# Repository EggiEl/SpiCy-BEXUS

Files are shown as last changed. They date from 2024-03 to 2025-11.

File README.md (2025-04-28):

# SpiCy-BEXUS
Please take a look at the [wiki](https://github.com/EggiEl/SpiCy-BEXUS/wiki) for documentation of electrical and software.

### About
This is the official GitHub repository of the SpiCy-BEXUS team, dedicated to code sharing and documentation for our project.

<table align="center">
  <tr>
    <td align="center">
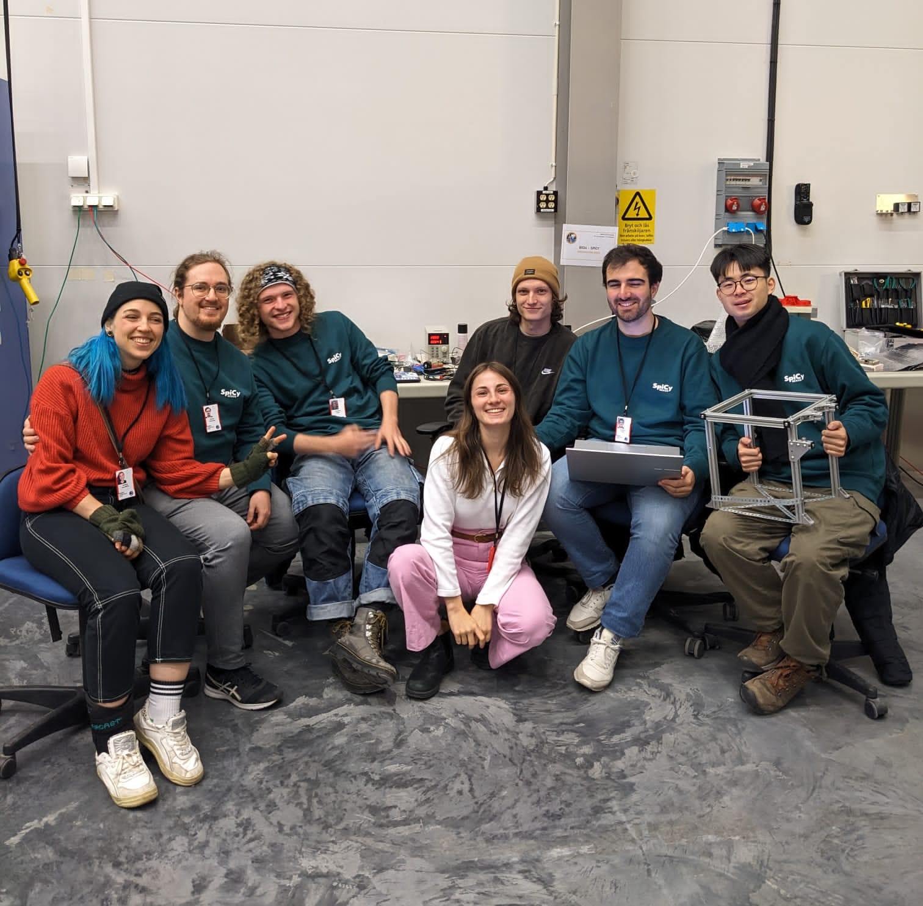
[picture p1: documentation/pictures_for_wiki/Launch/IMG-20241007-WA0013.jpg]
      
    </td>
    <td align="center">
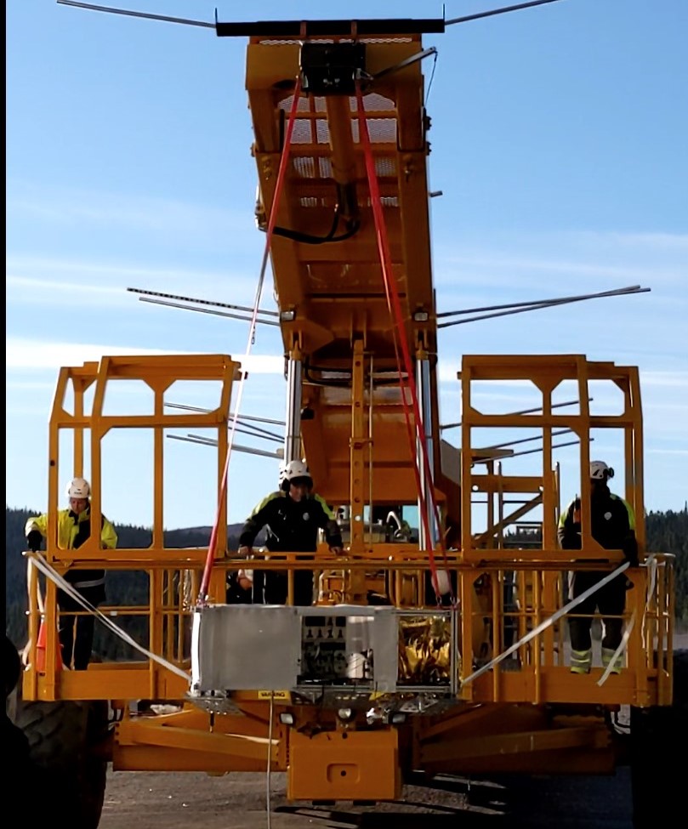
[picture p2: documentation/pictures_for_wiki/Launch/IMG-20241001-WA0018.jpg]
      
    </td>
    <td align="center">
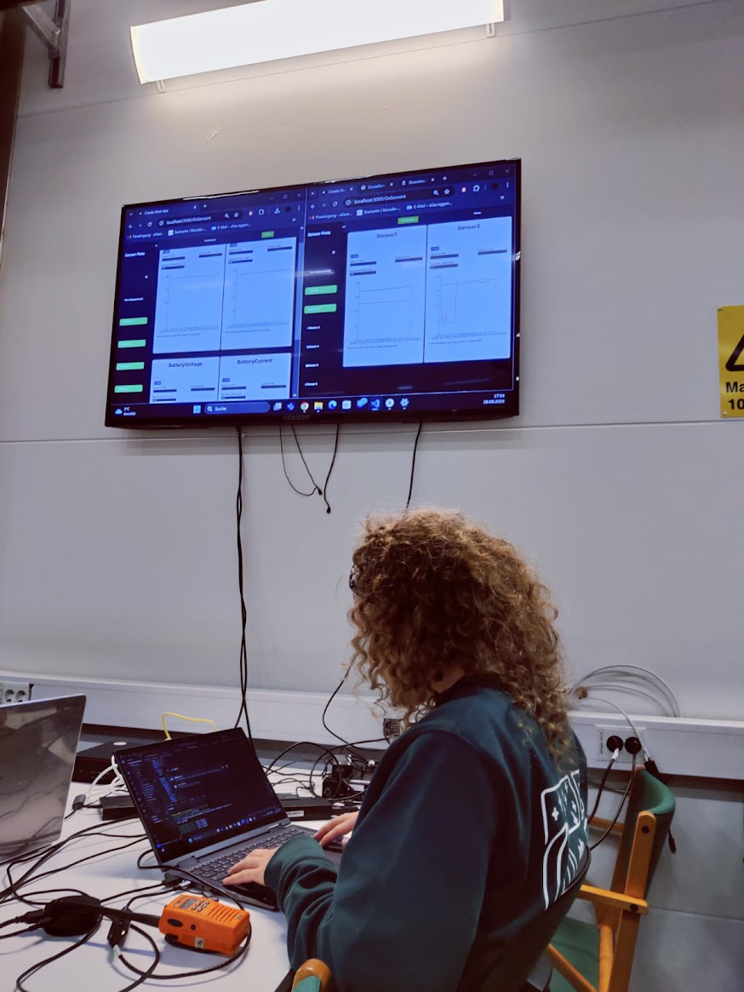
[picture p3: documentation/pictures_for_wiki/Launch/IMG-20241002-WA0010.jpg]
      
    </td>
  </tr>
  <tr>
    <td align="center">
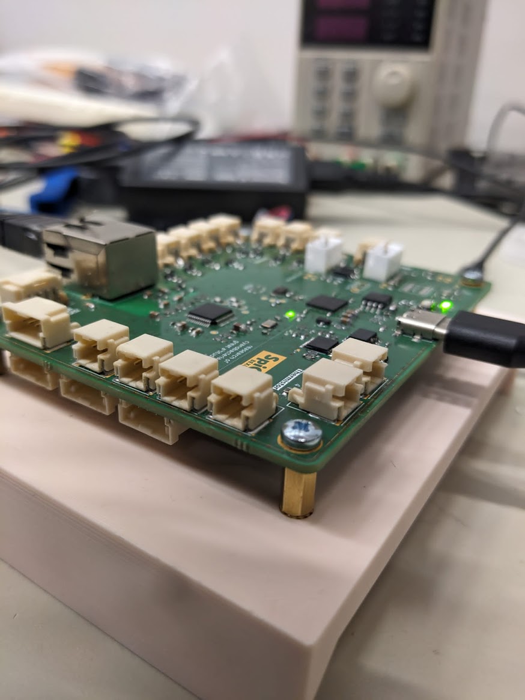
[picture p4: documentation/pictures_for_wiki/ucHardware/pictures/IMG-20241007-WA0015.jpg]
      
    </td>
    <td align="center">
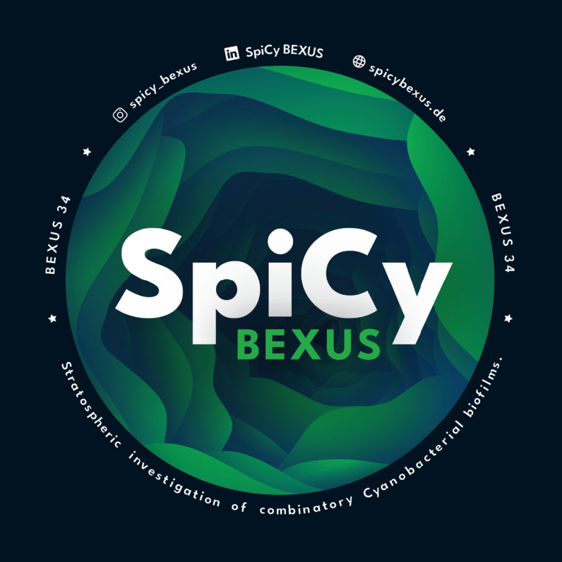
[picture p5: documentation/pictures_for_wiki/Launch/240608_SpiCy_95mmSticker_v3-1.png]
      
    </td>
    <td align="center">
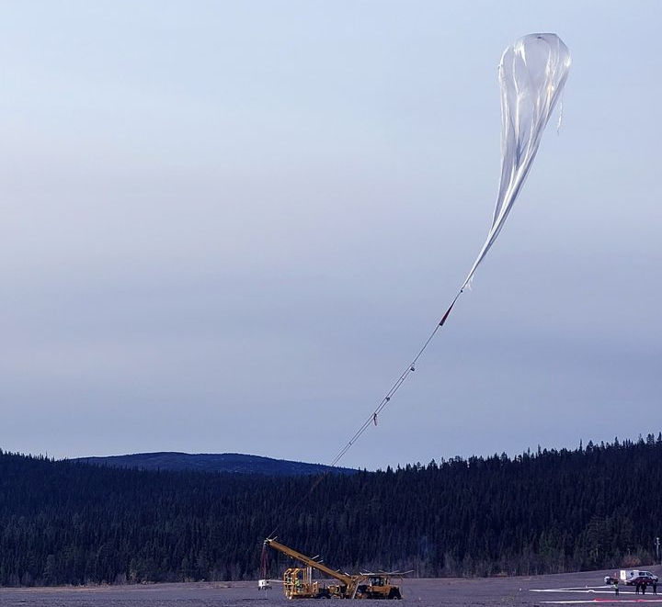
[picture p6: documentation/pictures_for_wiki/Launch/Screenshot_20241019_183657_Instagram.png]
      
    </td>
  </tr>
  <tr>
    <td align="center">
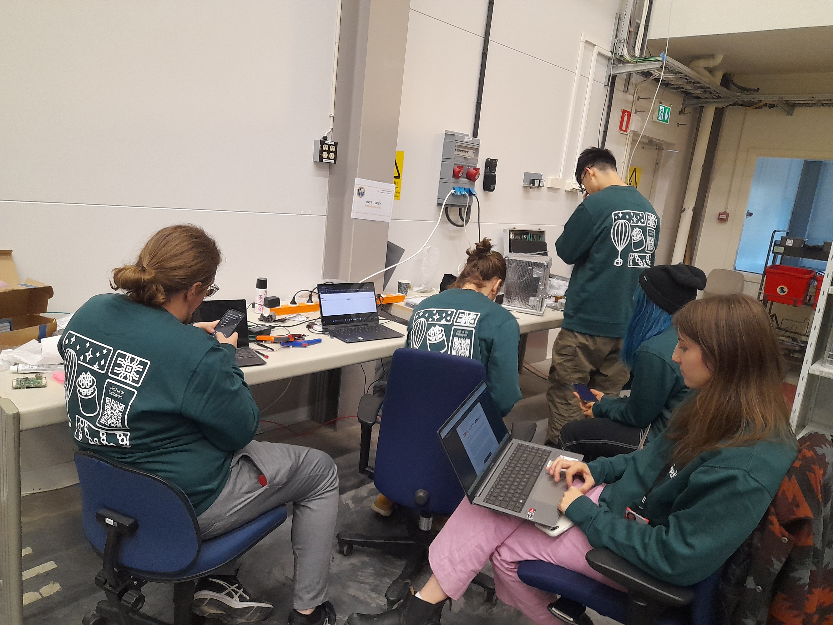
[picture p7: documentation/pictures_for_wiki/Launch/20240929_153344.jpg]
      
    </td>
    <td align="center">
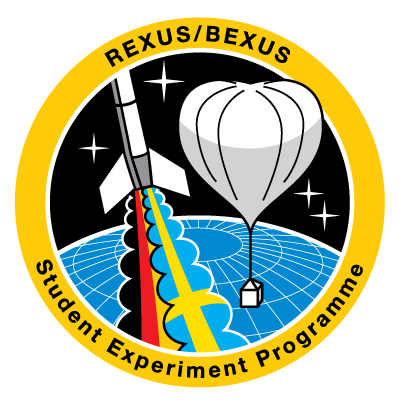
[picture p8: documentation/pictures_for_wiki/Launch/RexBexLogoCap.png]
RexBex Logo
      
    </td>
    <td align="center">
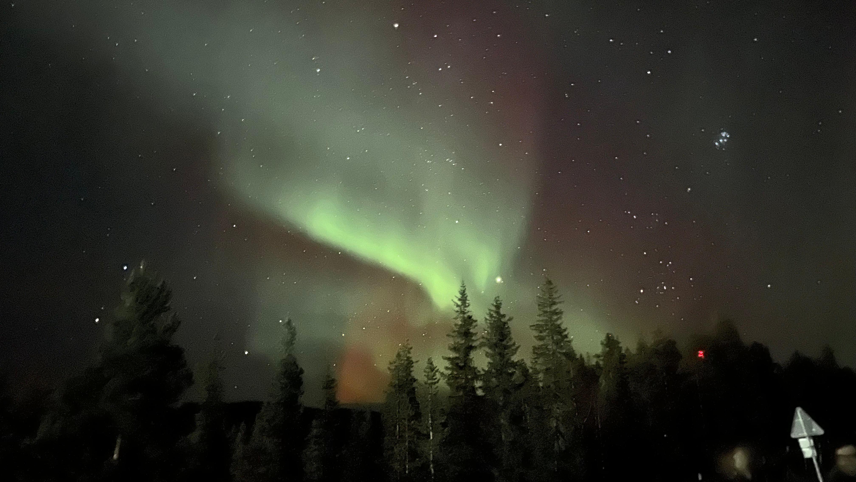
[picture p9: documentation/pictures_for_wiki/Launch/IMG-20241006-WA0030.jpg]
      
    </td>
  </tr>
</table>

### Project Overview
SpiCy (Stratospheric investigation of combinatory cyanobacterial biofilms) is a student-led mission to investigate the behavior of combinatory cyanobacterial biofilms under increased ionizing and non-ionizing radiation levels in the stratosphere to propose new alternatives of oxygen suppliance during space travel missions.

Cyanobacteria are among the oldest and most efficient photosynthetic organisms on planet Earth. They contribute 25% of the oxygen on Earth today and were crucial in forming our atmosphere in the early stages of Earth's development through oxygenation. As they are mostly aquatic or at least, need a certain degree of humidity, heterotrophic bacteria as a biofilm coordinator to mitigate their dependency are incorporated. These biofilms are a promising candidate in a plethora of space-related research (i.e. medicinal, life). Through forming adhesive biofilms, the bacteria are more resilient to radiation, thermal shocks, mechanical tearing and dry environments. 

Project SpiCy intends to capitalize on the cyanobacterial ability to produce oxygen with minimum requirements and research their viability in long-term oxygen generation for human space flight and colonization missions.

This github documents the technical side of things.

### Contact Us
Take a look at our [Website](https://spicybexus.de/)

### Setup
#### Node 
https://nodejs.org/en/download

#### MongoDB Community Server: 
https://www.mongodb.com/try/download/community

#### How to setup Project after cloning: 

In the root of the Project use:
```
pip install -r requirements.txt
npm install
```

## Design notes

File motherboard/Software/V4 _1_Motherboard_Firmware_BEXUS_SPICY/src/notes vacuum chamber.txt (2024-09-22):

Notes vacuum chamber test

Set up exel:
-start server
-convert bin to csv
-import data as csv
-transform ->Transformieren->Textspalte->analysis->JSON
-Import
-Use in Diagram

print status
/c h -1 0 0 0\n
/c g 0 0 0 0\n

Commands to switch to step response function:
disable all pi controllers
/c c 0 -100000.0  -1 -1 \n
/c c 1 -100000.0  -1 -1 \n
/c c 2 -100000.0  -1 -1 \n
/c c 3 -100000.0  -1 -1 \n
/c c 4 -100000.0  -1 -1 \n
/c c 5 -100000.0  -1 -1 \n

set all heaters to 100
/c h 0 100 \n
/c h 1 100 \n
/c h 2 100 \n
/c h 3 100 \n
/c h 4 100 \n
/c h 5 100 \n

reactivates pi controller with kp = 5
/c c 0 5 -1 -1 \n
/c c 1 5 -1 -1 \n
/c c 2 5 -1 -1 \n
/c c 3 5 -1 -1 \n
/c c 4 5 -1 -1 \n
/c c 5 5 -1 -1 \n

sets pi controller
/c c 0 ki i imax
/c c 1 ki i imax
/c c 2 ki i imax
/c c 3 ki i imax
/c c 4 ki i imax
/c c 5 ki i imax

/c e 0 T_SET Power
/c e 1 T_SET Power
/c e 2 T_SET Power
/c e 3 T_SET Power
/c e 4 T_SET Power
/c e 5 T_SET Power

set all heaters to 0
/c c 0 -100000.0  -1 -1
/c c 1 -100000.0  -1 -1
/c c 2 -100000.0  -1 -1
/c c 3 -100000.0  -1 -1
/c c 4 -100000.0  -1 -1
/c c 5 -100000.0  -1 -1
/c h 0 0
/c h 1 0
/c h 2 0
/c h 3 0
/c h 4 0
/c h 5 0

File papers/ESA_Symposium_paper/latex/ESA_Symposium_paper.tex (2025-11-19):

\documentclass[journal]{IEEEtran}

\usepackage[utf8]{inputenc}
\usepackage[T1]{fontenc}
\usepackage{graphicx}
\usepackage{amsmath}
\usepackage{amssymb}
\usepackage{hyperref}
\usepackage{siunitx}
\usepackage{booktabs}
\usepackage[acronym,style=long]{glossaries}
\usepackage{wrapfig}

\usepackage[
    backend=biber,
    style=ieee,
    citestyle=numeric
]{biblatex}
\addbibresource{references.bib}

\makeglossaries

\newacronym{er}{\ensuremath{\epsilon_r}}{relative permittivity}
\newacronym{ereff}{\ensuremath{\epsilon_{r,eff}}}{effective relative permittivity}
\newacronym{tantheta}{\ensuremath{\tan{\theta}}}{dielectric loss tangent}

\title{Challenges of a high altitude experiment\\ as an interdisciplionary team}
\title{Empirical evaluation of\\ oxygen production in high altitude}
\author{Alexander Kubryk, Pablo Martin Carrilero, Tian Lan, Jayanth Narra, Ilana Schürmeyer, Eva-Maria Sontag, Fynn Gewiese, Sibtain Ali Thepdawala, Amanda Clot, Elias Eggenberger, Jacqueline Wiethaler, Runjjia Zhao}

\begin{document}

\maketitle

\begin{wrapfigure}{l}{0.08\textwidth}
	\centering
	% \includegraphics[width=\linewidth]{./pics/REXUS_BEXUS_Logo_article-3055423975.jpg}
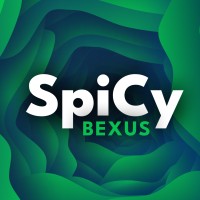
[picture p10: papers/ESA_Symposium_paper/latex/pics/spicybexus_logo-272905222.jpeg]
	
	% \caption{SpiCy Logo}
\end{wrapfigure}

\begin{abstract}
	SpiCy (Stratospheric investigation of combinatory cyanobacterial biofilms) is a student-led mission to investigate the behavior of combinatory cyanobacterial biofilms under increased ionizing and non-ionizing radiation levels in the stratosphere to propose new alternatives of oxygen suppliance during space travel missions.

	Project SpiCy intends to capitalize on the cyanobacterial ability to produce oxygen with minimum requirements and research their viability in long-term oxygen generation for human space flight and colonization missions.
\end{abstract}

\section{Biology}

Cyanobacteria are among the oldest and most efficient photosynthetic organisms on planet Earth. They contribute 25\% of the oxygen on Earth today and were crucial in forming our atmosphere in the early stages of Earth’s development through oxygenation. As they are mostly aquatic or at least, need a certain degree of humidity, heterotrophic bacteria as a biofilm coordinator to mitigate their dependency are incorporated. These biofilms are a promising candidate in a plethora of space-related research (i.e. medicinal). Through forming adhesive biofilms, the bacteria are more resilient to radiation, thermal shocks, mechanical tearing and dry environments.
\section{Mechanical design}

\begin{wrapfigure}{l}{0.4\linewidth}
	\centering
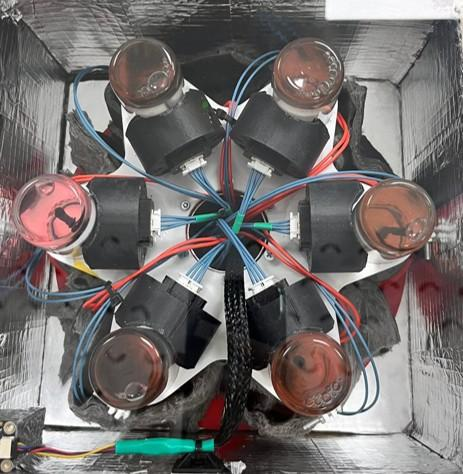
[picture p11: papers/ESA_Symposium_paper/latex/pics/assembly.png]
	
	\caption{tube assembly}
\end{wrapfigure}
% \begin{figure}[ht]
% 	\centering
% 	\includegraphics[width=0.5\linewidth]{./pics/assembly.png}
% 	% \caption{Aproximation from \cite[269]{johnson_blackmagic}}
% \end{figure}

The mechanical design includes a styrofoam container housing individual biofilm tubes, each slot tailored to tube dimensions for stability and insulation. An aluminum profile cage reinforces the outer box for structural integrity and protection. A thermal control system regulates conditions for biofilm growth, with sensors providing real-time feedback for adjustments. A transparent plexiglass lid allows sunlight and visual inspection, securely attached for contamination prevention. An electronics compartment, made of durable plexiglass, organizes internal components with convenient access points for maintenance. Materials like styrofoam and quartz glass are chosen for their insulating and transparent properties, respectively, ensuring optimal functionality.

\section{Electrical design}
The electronic core of the system is orchestrated by a microcontroller, specifically an RP2040 This microcontroller serves as the brain, overseeing and coordinating all system operations. It reads in sensor data and adjusts the Power of the Heating elements according to this.

\begin{figure}[ht]
	\centering
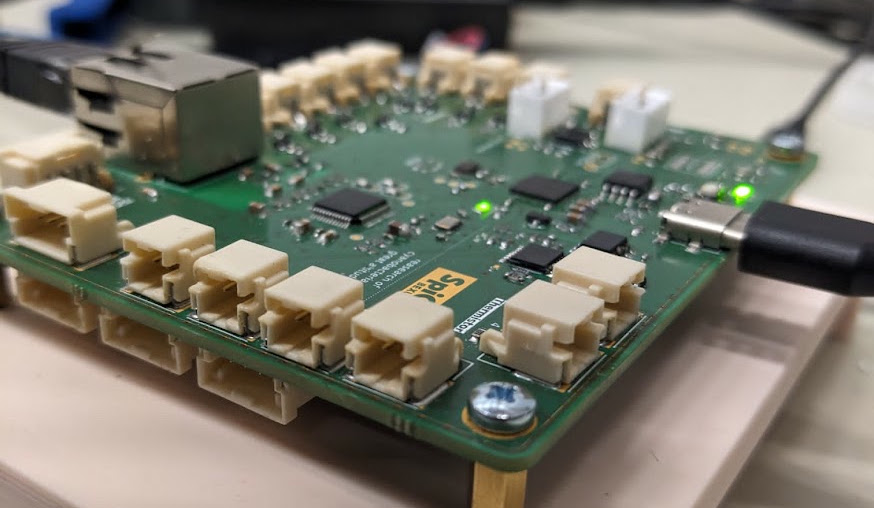
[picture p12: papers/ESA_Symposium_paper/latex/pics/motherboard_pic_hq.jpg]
	
	\caption{motherboard}
\end{figure}

All data management will happen with one central data container, a struct named packet. It contains Sensordata, status, a timestamp and the pid values of the temperature system. It will be saved locally on the SD card and transmitted to a laptop via the ethernet connection.

\section{Software}
The embedded software architecture is implemented on the
microcontroller in C++, covering essential functionalities like
thermal control, sensor data acquisition and uplink/downlink
communication processes. The thermal control is
implemented as a PI controller, which controls the heating via
PWM.
For ground station operations, the system will utilize a tech
stack consisting of a Node.js backend communicating with a
MongoDB database, complemented by a Web-based
Localhost Application frontend.

\newpage
\section{Flight data}
\begin{figure}[ht]
	\centering
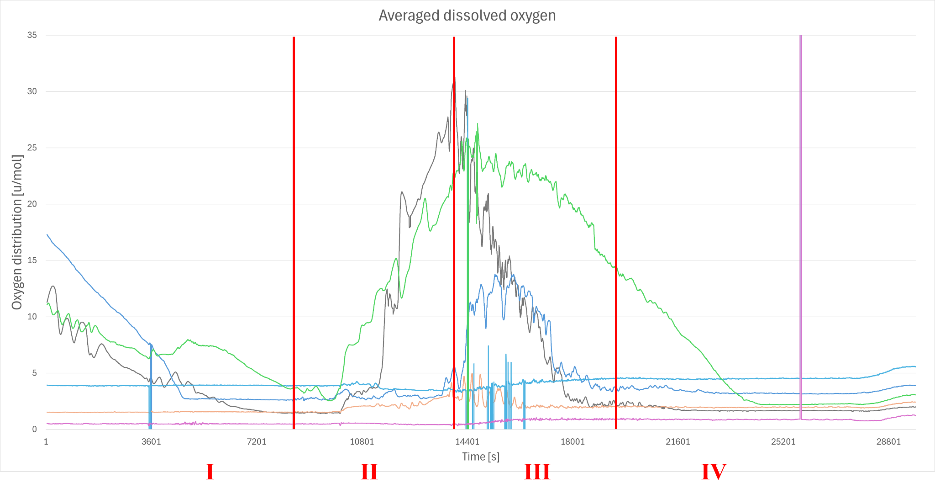
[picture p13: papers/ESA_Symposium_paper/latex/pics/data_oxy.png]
	
	\caption{measurement of dissolved oxygen}
\end{figure}

Fig. 7.3-1 shows the measurement of dissolved oxygen, revealing significant differences between the samples during flight. Oxygen trends were averaged over 40 time points to compensate for single corrupted data points.

Sample colors represent the following conditions:
Light Blue: Nostoc sp. with B. subtilis
Blue: Nostoc sp. with P. taiwanensis
Green: Nostoc sp. with E. coli
Black: Pure culture Nostoc sp.
Orange: Scraped Nostoc sp. with E. coli from a previous cultivation batch
Magenta: Medium control

During launch preparation (I), samples were not exposed to light and oxygen production continued to decline. Mechanical movement of the gondola during transport and mounting may have contributed to this effect, as abrupt shaking could cause dissolved oxygen to form bubbles that could no longer be detected by the oxygen sensors.

At late access (II), the light cover was removed shortly before launch. Pure Nostoc sp. (Black) and Nostoc sp. with E. coli (Green) immediately resumed oxygen production once light reached the samples (see ambient light measurement in Fig. 7.2-8). The other samples showed no significant change in oxygen production, suggesting a resting state caused by stress or insufficient light penetration due to the biofilms sinking to the bottom of the glass tubes.

Shortly after launch during ascent (III), pure Nostoc sp. (Black) rapidly lost oxygen production. Surprisingly, the Nostoc sp. with P. taiwanensis sample (Blue) displayed increased dissolved oxygen levels immediately after launch. This is likely explained by either light finally reaching the previously sunken biofilm or partial dissolution of the biofilm into the medium, and not necessarily an effect related to biofilm activity.

Most notably, Nostoc sp. with E. coli (Green) maintained stable oxygen levels throughout ascent, indicating continued oxygen production despite changing altitude, increased mechanical stress, and variable light exposure. A gradual reduction over time was expected, as the stratospheric environment provides non-optimal growth conditions and the organisms reduce metabolic activity in response.

During the float phase (IV), Nostoc sp. with E. coli (Green) continued to show delayed oxygen decline, confirming sustained oxygen production. The expected decrease due to heterotrophic respiration by E. coli was not detected. Further analysis is required to investigate the presence and functional role of heterotrophic bacteria within the final biofilms. As described in Chapter 1.1, heterotrophic bacteria may contribute to maintaining the biofilm, promoting its initial formation, or conditioning surfaces for cyanobacterial attachment.

The medium control (Magenta) showed no change in oxygen data during preparation, flight, or descent, confirming proper sensor function and absence of contamination in BG11 medium. The samples Nostoc sp. with B. subtilis (Light Blue) and scraped Nostoc sp. with E. coli (Orange) showed low oxygen readings even prior to launch. This was attributed to a missing calibration step caused by repeated disassembly during launch delays.

No leakage, contamination, or visible structural damage was observed in the biomodule or glass tubes. All biological samples survived the flight and continued growing in the laboratory post-recovery, except for the scraped Nostoc sp. with E. coli sample (Orange), which died two weeks after return.

In conclusion, pure Nostoc sp. showed an immediate and pronounced drop in oxygen production during flight, unlike the co-cultivated Nostoc sp. with E. coli. These results provide initial evidence that co-cultivation with heterotrophic bacteria may enhance resilience and support stable biofilm formation in cyanobacteria under extreme environmental stress.

\section{Lessons learned}
The project taught us several valuable lessons, beginning with the
unexpected challenge of securing lab space. Initially, no professors had the
resources to accommodate us, leaving us at an impasse. However, by
reaching out to the dean and fostering connections with other universities, we
successfully resolved this issue. Today, a dedicated lab space is available for
our work, underscoring the importance of persistence and networking.
Coordinating across sub-teams proved to be another significant challenge,
largely due to the diversity of expertise required by the project. Effective
communication between specialties took time to develop, but it became a
crucial skill for our team. To prevent such difficulties in the future, we have
adopted the SCRUM methodology to streamline collaboration. We also
realized that unclear requirements further exacerbated these communication
issues. Establishing better-defined and mutually agreed-upon requirements165
not only improved coordination but also laid a stronger foundation for the
project.
A gap in expert knowledge became apparent during the experimental design
phase, highlighting the need for specialized guidance. By collaborating
extensively within the team and consulting external experts, we were able to
refine our experimental approach. This experience emphasized the value of
seeking diverse perspectives when faced with complex challenges.
Securing funding and sponsorship presented another hurdle, particularly in
the project's early stages. With time, support from LMU alleviated many of
these concerns. Nevertheless, bureaucratic complications in using LMU funds
for travel costs persist, prompting us to actively seek additional sponsors to
cover these specific needs.
On a technical front, the team acquired new skills, including soldering QFN
components and cultivating cyanobacteria. While mastering these techniques
involved overcoming initial challenges, conversations with experts and
consistent practice helped us refine our methods. These skills not only
advanced the project but also enriched the team’s technical repertoire.
The outreach team grappled with balancing high-quality content production
against the constraints of limited resources. Academic seminars had not
prepared us for such practical limitations, so we adapted by developing
flexible, cost-efficient approaches. This shift required creative problem-solving
but proved essential for sustaining our public engagement efforts.
Sensor selection also brought its share of challenges, particularly in
identifying the optimal temperature sensor from numerous options. Through
rigorous testing, we addressed this issue. Furthermore, lessons learned
during the launch campaign underscored the critical importance of thorough
labeling and documentation. A lack of visible labeling for tubes and sensors
created significant difficulties during analysis, a mistake we now recognize as
preventable. Moving forward, we will ensure that all components are labeled
clearly and visibly, both on the hardware and within the user interface of the
ground station.
Defining project requirements was another area where clarity proved
essential. A deeper understanding of the components and their
interdependencies emerged as critical to achieving a design that met
expectations. Through iterative refinement, we have gained confidence in
establishing comprehensive requirements.
Simulating the unique experimental environment posed challenges during the
verification process, requiring innovative and non-traditional approaches. By
thinking creatively, we developed methods to address these difficulties
effectively. Similarly, careful planning before conducting experimental tests
helped anticipate potential issues, saving time and resources in the long run.
Mechanical design was another iterative process, where each cycle of
refinement provided opportunities for improvement. This iterative approach,
though time-intensive, proved indispensable in achieving the desired
functionality.
In summary, the project taught us resilience, adaptability, and the importance
of meticulous planning and collaboration. Every challenge we faced became
an opportunity to learn, ultimately strengthening our team and the project as a
whole.

\printbibliography

\printglossaries

\begin{figure}[ht]
	\centering
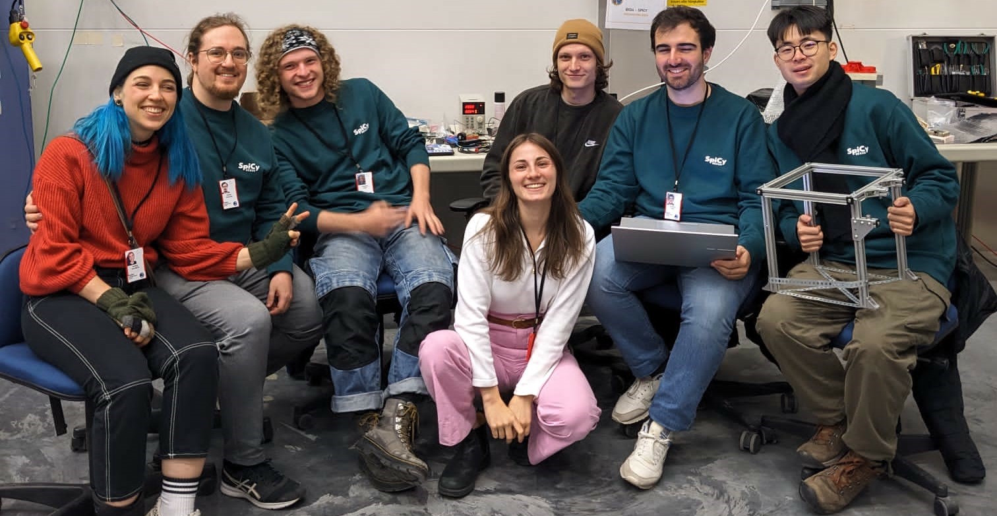
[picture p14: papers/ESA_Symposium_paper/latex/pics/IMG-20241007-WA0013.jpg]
	
	\caption{The team}
\end{figure}
\end{document}

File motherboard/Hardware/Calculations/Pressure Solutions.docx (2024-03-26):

Pressure Solutions

1 Passive
  1.1 Vent(s)

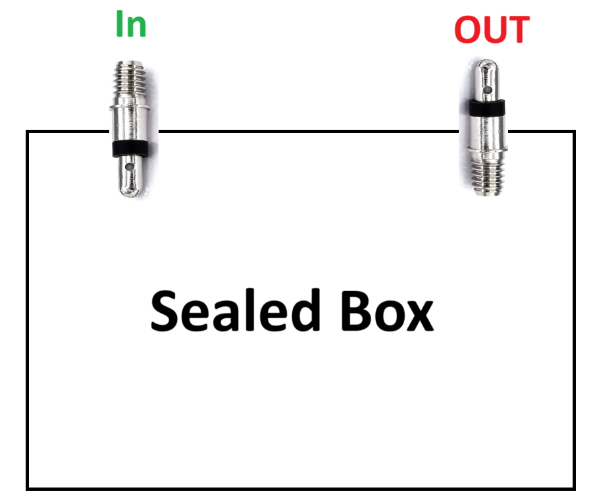
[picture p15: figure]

Releasing pressure upon ascent and taking air in trough the descent. Vents block outside air so thermal stability via ascent is possible.

Pro | Contra
- Super easy - Cheap - Reliable | - Lets in air on the descent, cooling difficult (but not impossible if good managed)

  1.2 Variable Volume Chamber

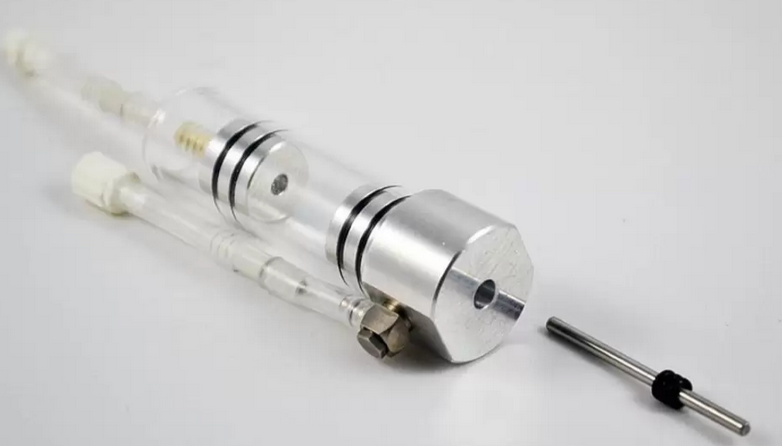
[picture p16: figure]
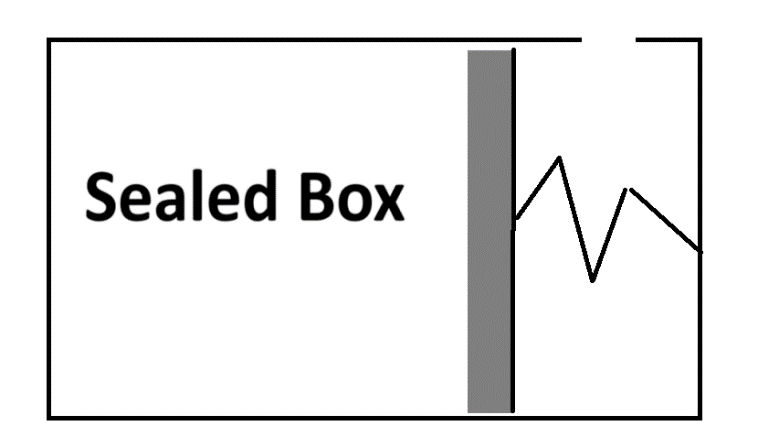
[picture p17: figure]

A flexible chamber or bag inside the payload can expand or contract with changes in pressure. This helps to minimize pressure differentials and maintain a more constant internal pressure.

Pro | Contra
- Constant temperature -> no cooling on the descent | - Complex - Expensive

Maybe possible with a modified hydraulic car brake system?

  1.3 Membrane

A flexible membrane or diaphragm can separate the payload into two sections. As pressure changes, the membrane flexes, helping to equalize pressure differentials.

This Membrane would be one of the walls of the payload.

- Difficult to find a suitable membrane
- Huge Thermal losses
- Hard to engineer to reliability
  1.4 Vacuum chamber

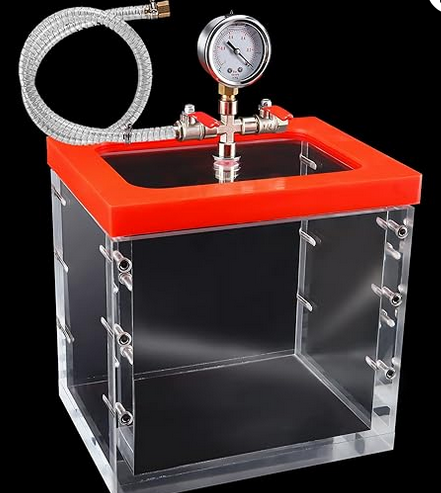
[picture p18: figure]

The experiment is contained in a (probably glass) container and pressurized to the pressure between min and max amplitude.

Pro | Contra
- Reliable - Giga Chad in terms of heating | - Power/electric contacts very difficult (wireless transmission?) - Could heat up too much. (bad) - very expensive

  1.5 Hole

Like vent but worse because of dissipating of heat.

2 Aktive
  2.1 Pump

Bad Idea. We don´t have the power and its complicated.

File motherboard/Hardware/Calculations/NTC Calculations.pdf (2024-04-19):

NTC Resistor

Constans:
B-Constant | 3977 | Temperature Resistance
R at 25°C | 10000 | 0 | 33900,4209
5 26093,9205
10 20271,5946
15 15886,9982
20 12554,7025
Formulars: | 25 | 10000
30 8025,14518
35 6486,44088
40 5278,52005
45 4323,45404
50 3563,13194
55 2953,87922
60 2462,62387

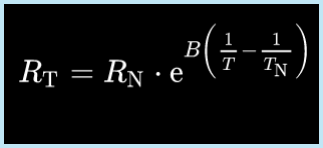
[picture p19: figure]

0 °C + 273,15 = 273,15 K | 65 | 2064,14174
70 1739,0614
80 1252,5298
100 684,938723
150 194,411188
200 72,0085807
250 32,2475864
300 16,6142994

Voltage Divider

Constants: | Temperature Voltage
VCC (ntc+) | 3,00 | 0 | 0,39230346
R9 | 5100 | 5 | 0,49048019
10 0,6030366
15 0,72902279
20 0,86662463
25 1,01324503
30 1,16570139
35 1,32050905
40 1,47419863
45 1,62360849
50 1,76610493
55 1,89970567
60 2,02310736
65 2,13563614
70 2,23714909

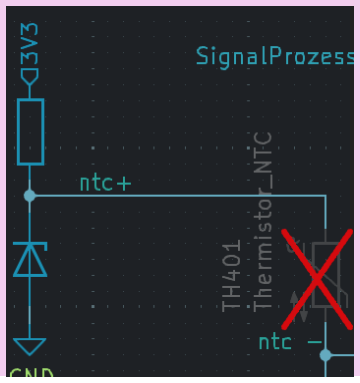
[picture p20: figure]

80 2,40848929
100 2,64479897
150 2,88983977
200 2,95823175
250 2,98115002
300 2,99025862

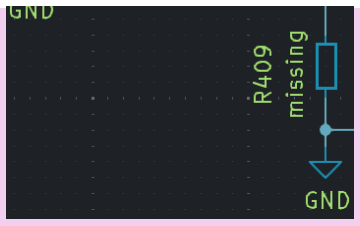
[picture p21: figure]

Signal Prozessing

Constans
Gain | 2 | Vairables
Voff | 0,4 | R3 | 65000
VCCoff (ntc+) | 3 | R4 | 10000
R1 | 5100
R2 | 10000
ADC Resul [bit] | 12
ADC Vref | 3

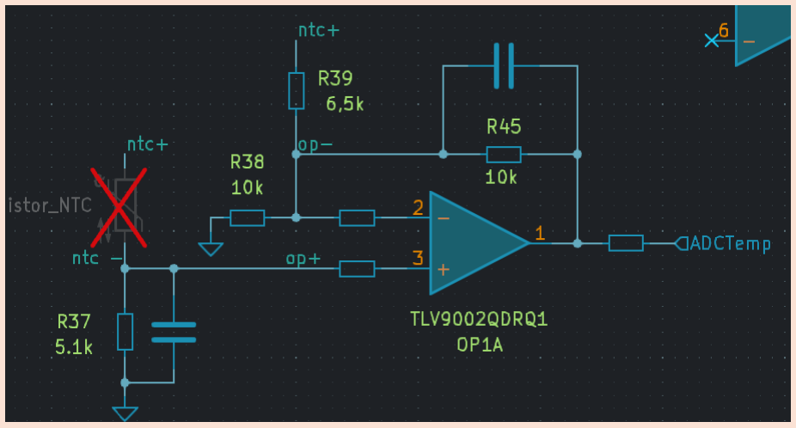
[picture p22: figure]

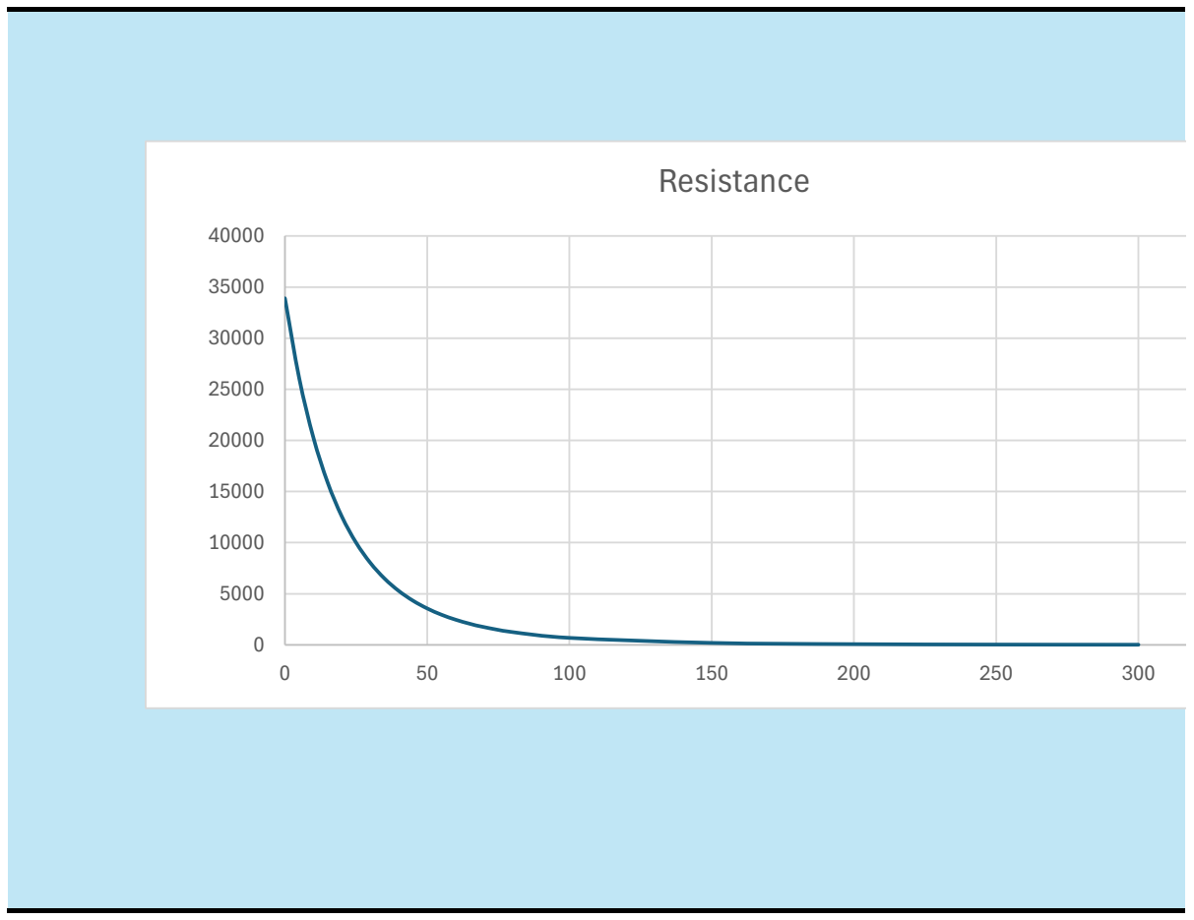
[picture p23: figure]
Resistance
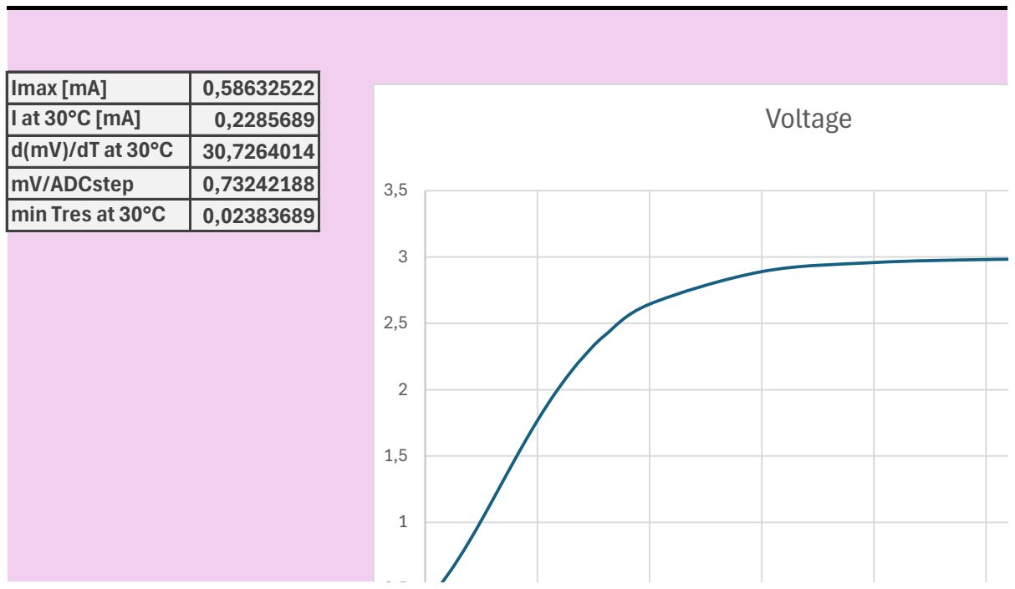
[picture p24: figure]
Imax [mA]; mV/ADCstep; min Tres at 30°C; Voltage

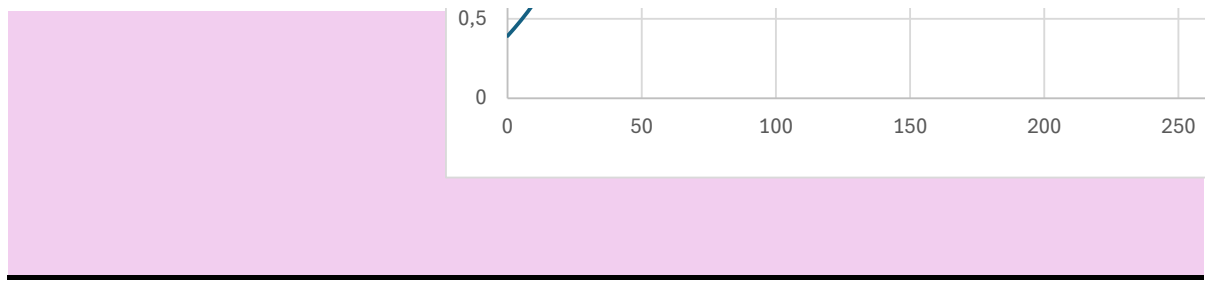
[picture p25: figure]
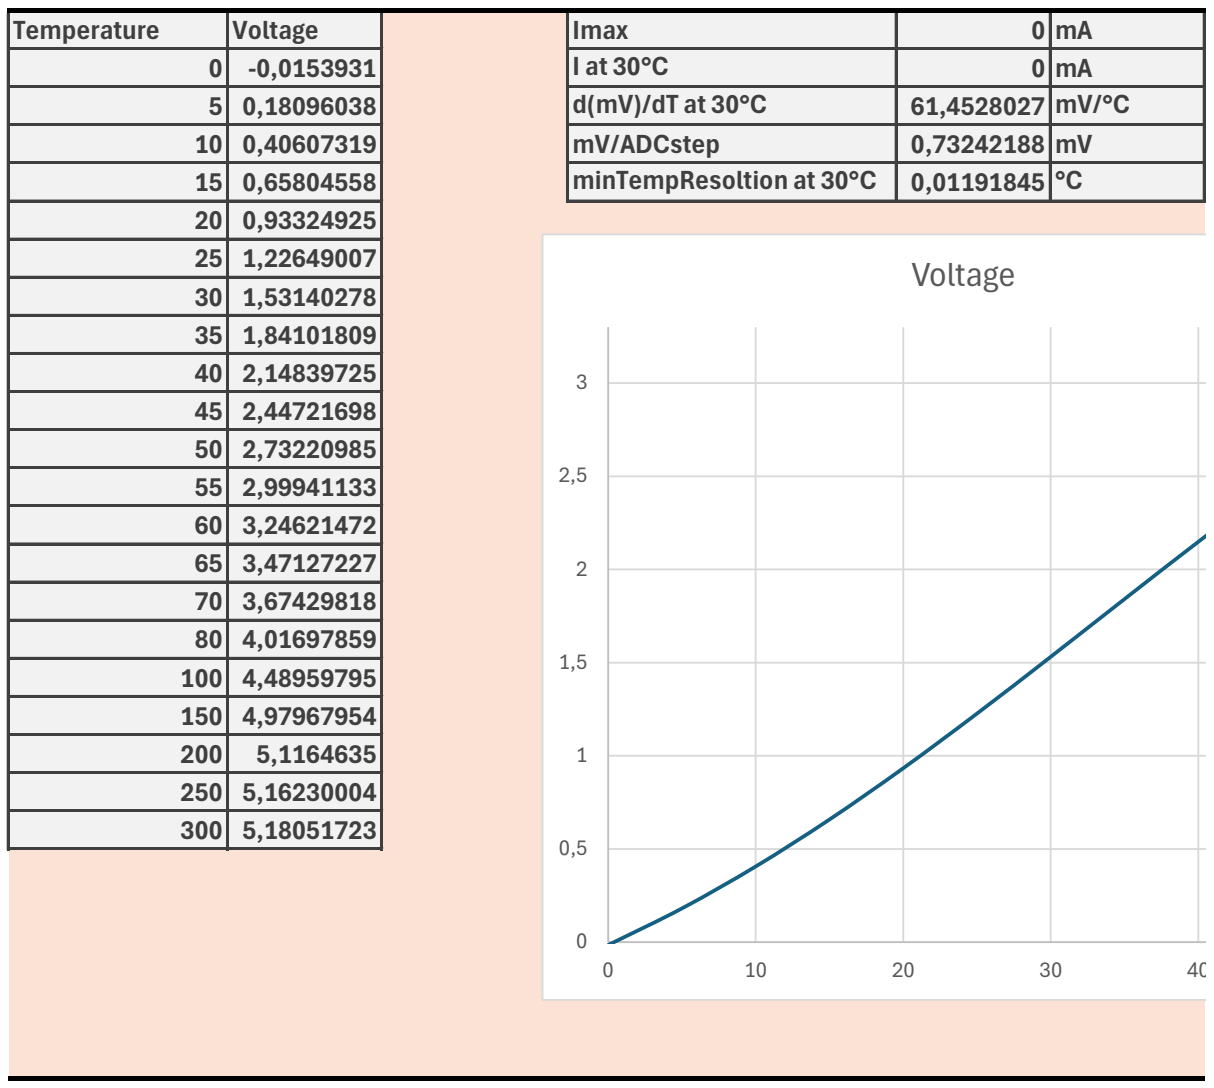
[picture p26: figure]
Temperature; Voltage; Imax; mV/ADCstep; minTempResoltion at 30°C

350

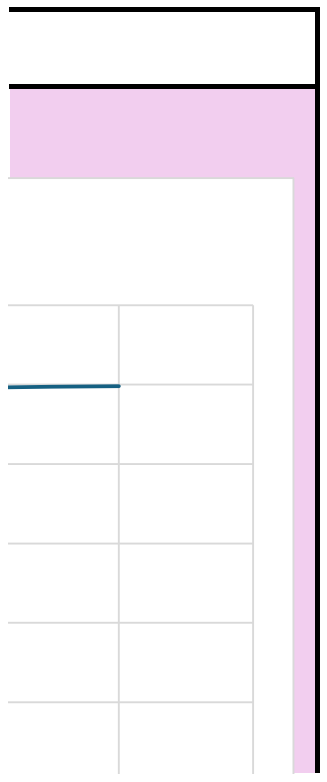
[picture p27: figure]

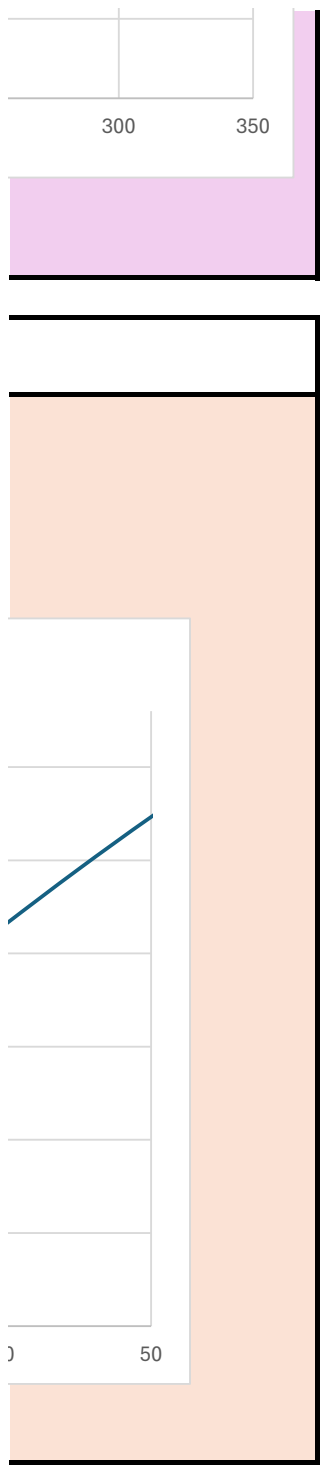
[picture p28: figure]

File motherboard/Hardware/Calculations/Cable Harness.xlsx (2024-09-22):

Cable Harness
 |  | nType | nCables | length per cable(m) | Total length
 | OxygenSensors | 6 | 4 | 0.4 | 9.6
 | Heater | 6 | 2 | 0.04 | 0.48
 | GPIOs | 2 | 4 | 0.5 | 4
 | PowerConnector | 1 | 2 | 0.3 | 0.6
 | Testing | 1 | 8 | 0.4 | 3.2
 |  |  |  | Savety factor | 1.2
 |  |  |  | SUMME (m) | 21.456
 |  |  |  | ft | 70.39370304
 |  |  |  | nPins | 103.2

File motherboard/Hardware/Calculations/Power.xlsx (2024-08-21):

Power calculations |  |  | - all values in W
Power provider |  |  | Voltage converter |  |  |  |  | Voltage stabiliser |  |  |  |  | Power consumer
Component | Power_load | Power_idle | Component | Describtion | Efficiency | Power_load incl. Efficiency | Power_idle incl. Efficiency | Component | Describtion | Efficiency | Power_load incl. efficiency | Power_idle incl. Efficiency | Component | Description | Power_load | Power_idle
Vbatt | 35.02453909 | 0.5339533513 | -> |  |  |  |  |  |  |  |  |  | APTD2012LSURCK | wrong battery polarity detection LED | doesn´t matter | doesn´t matter
 |  |  | LM2596S | Buck converter Vsys | 0.9 | 2.415803842 | 0.5339137513 | NCP1117ST33T3G | LDO uC | 0.55 | 0.3441878182 | 0.3141818182 | Rp2040 | Microcontroller | 0.0924 | 0.0924
 |  |  |  |  |  |  |  |  |  |  |  |  | APTD2012LCGCK | green LED + Resistor | 0.0066 | 0.0066
 |  |  |  |  |  |  |  |  |  |  |  |  | W25Q128JVS | Flash | 0.0825 | 0.066
 |  |  |  |  |  |  |  |  |  |  |  |  | TMUX1108PWR | Mux NTCs | 3.3e-06
 |  |  |  |  |  |  |  |  |  |  |  |  | TLV9002QDRQ1 | OpAmp NTCs | 0.0066 | 0.0066
 |  |  |  |  |  |  |  |  |  |  |  |  | LM4040BIM3-3.0_NOPB | V_Ref uC | 0.0006 | 0.0006
 |  |  |  |  |  |  |  |  |  |  |  |  | LM4040BIM3-3.0_NOPB | V_Ref NTCs | 0.0006 | 0.0006
 |  |  |  |  |  |  |  | NCP1117ST33T3G | LDO Lan/SD | 0.55 | 1.83 | 0.05770491803 | W5500 | ethernet controller | 0.4356 | 0.0429
 |  |  |  |  |  |  |  |  |  |  |  |  | kigsman 8GB | micro Sd | 0.495 | 0.0033
 |  |  |  |  |  |  |  | NCP1117ST33T3G | LDO Extern | 0.55 | 0 | 0.1086 | OXY | All 6 Oxygen Sensor. Under load: alway just one, P_load = P_one_load + 5 * Pidle | 0.0759 | 0.0594
 |  |  |  |  |  |  |  |  |  |  |  |  | CD4097B | MUX OXY | 0.00033 | 0.00033
 |  |  |  |  |  |  |  |  |  |  |  |  |  | Light sensor
 |  |  | DONGKER 280W/12A | Buck converter Vheat | 0.92 | 32.60873525 | 3.96e-05 | -> |  |  |  |  | INA240A3EDRQ1 | Heater Mosfet | 0 | 0
 |  |  |  |  |  |  |  |  |  |  |  |  |  | Kapton Heaters | 30 | 0
Variables:
VSYS[V] | 6
Heater[W] | 5

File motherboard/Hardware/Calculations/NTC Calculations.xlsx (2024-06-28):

NTC Resistor
 | Constans:
 | B-Constant | 3977 |  |  | Temperature | Resistance
 | R at 25°C | 10000 |  |  | 0 | 33900.42085
 |  |  |  |  | 5 | 26093.92054
 |  |  |  |  | 10 | 20271.59456
 |  |  |  |  | 15 | 15886.99821
 |  |  |  |  | 20 | 12554.70253
 | Formulars: |  |  |  | 25 | 10000
 |  |  |  |  | 30 | 8025.145179
 |  |  |  |  | 35 | 6486.440879
 |  |  |  |  | 40 | 5278.520053
 |  |  |  |  | 45 | 4323.454038
 |  |  |  |  | 50 | 3563.131937
 |  |  |  |  | 55 | 2953.879223
 |  |  |  |  | 60 | 2462.623865
 | 0 °C + 273,15 = 273,15 K |  |  |  | 65 | 2064.141744
 |  |  |  |  | 70 | 1739.061403
 |  |  |  |  | 80 | 1252.529796
 |  |  |  |  | 100 | 684.9387231
 |  |  |  |  | 150 | 194.4111881
 |  |  |  |  | 200 | 72.00858066
 |  |  |  |  | 250 | 32.24758636
 |  |  |  |  | 300 | 16.61429942
Voltage Divider
 | Constants: |  |  | Temperature | Voltage |  | Imax [mA] | 0.5863252191
 | VCC (ntc+) | 3.00 |  | 0 | 0.3923034589 |  | I at 30°C [mA] | 0.2285689003
 | R9 | 5100 |  | 5 | 0.4904801876 |  | d(mV)/dT at 30°C | 30.72640136
 |  |  |  | 10 | 0.6030365953 |  | mV/ADCstep | 0.732421875
 |  |  |  | 15 | 0.7290227905 |  | min Tres at 30°C | 0.02383689084
 |  |  |  | 20 | 0.8666246275
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

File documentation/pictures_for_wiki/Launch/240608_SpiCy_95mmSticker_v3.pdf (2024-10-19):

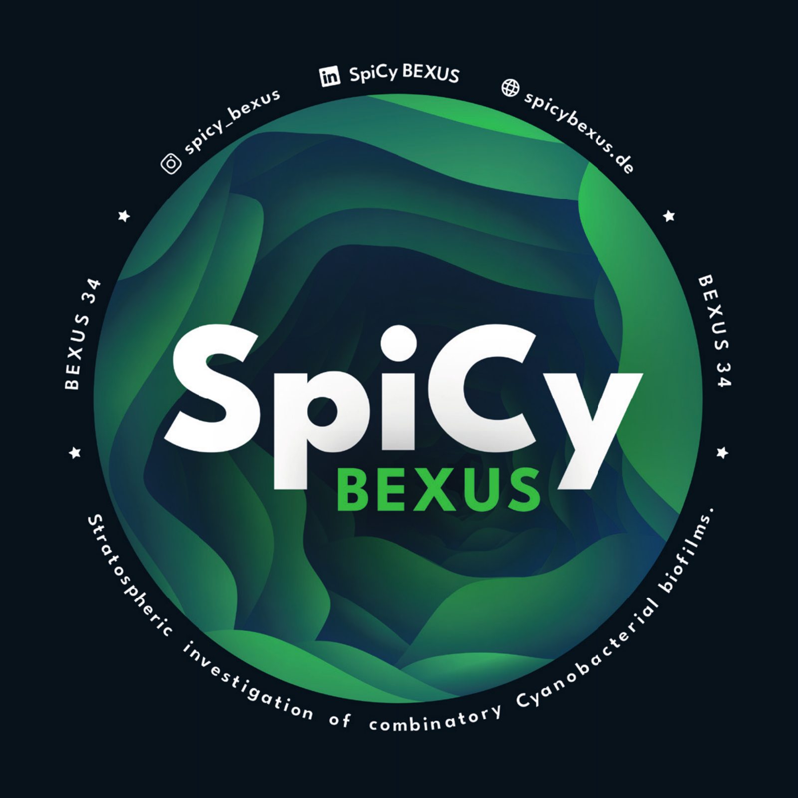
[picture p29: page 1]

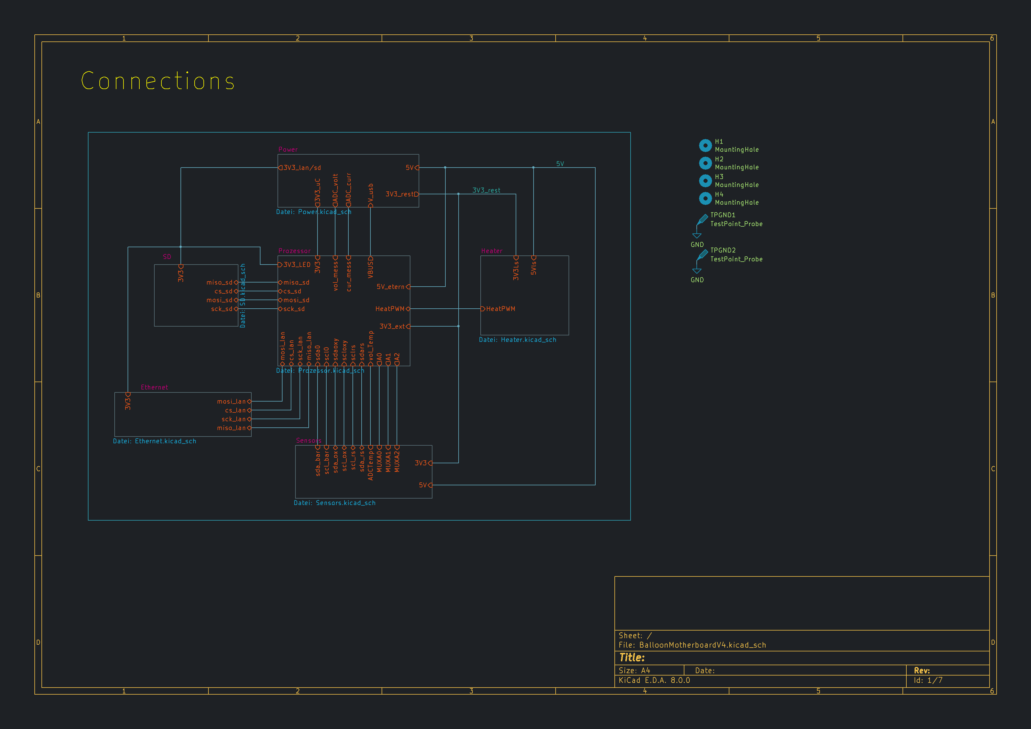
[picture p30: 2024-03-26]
documentation/pictures_for_wiki/ucHardware/pictures/Motherboard_V4_25_3_24-1.png

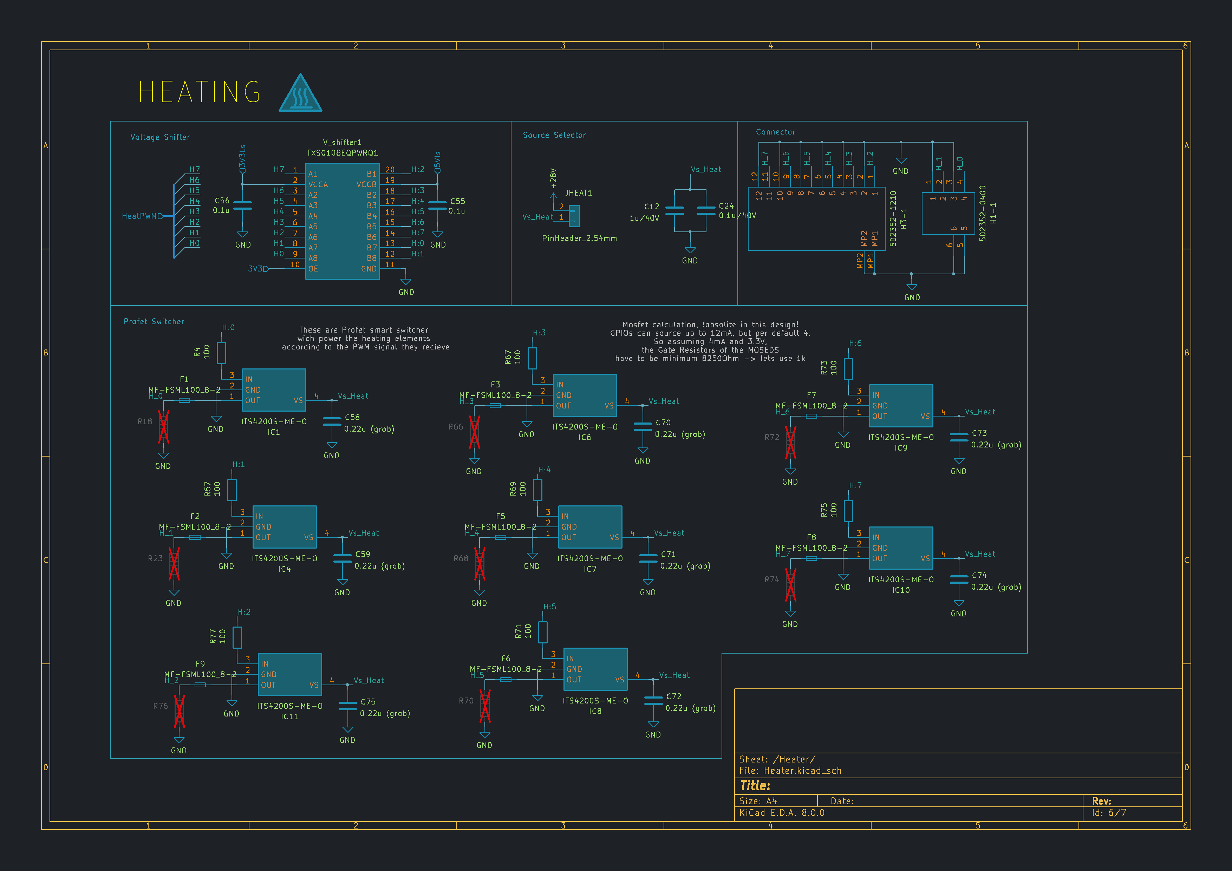
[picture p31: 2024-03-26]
documentation/pictures_for_wiki/ucHardware/pictures/Motherboard_V4_25_3_24-6.png

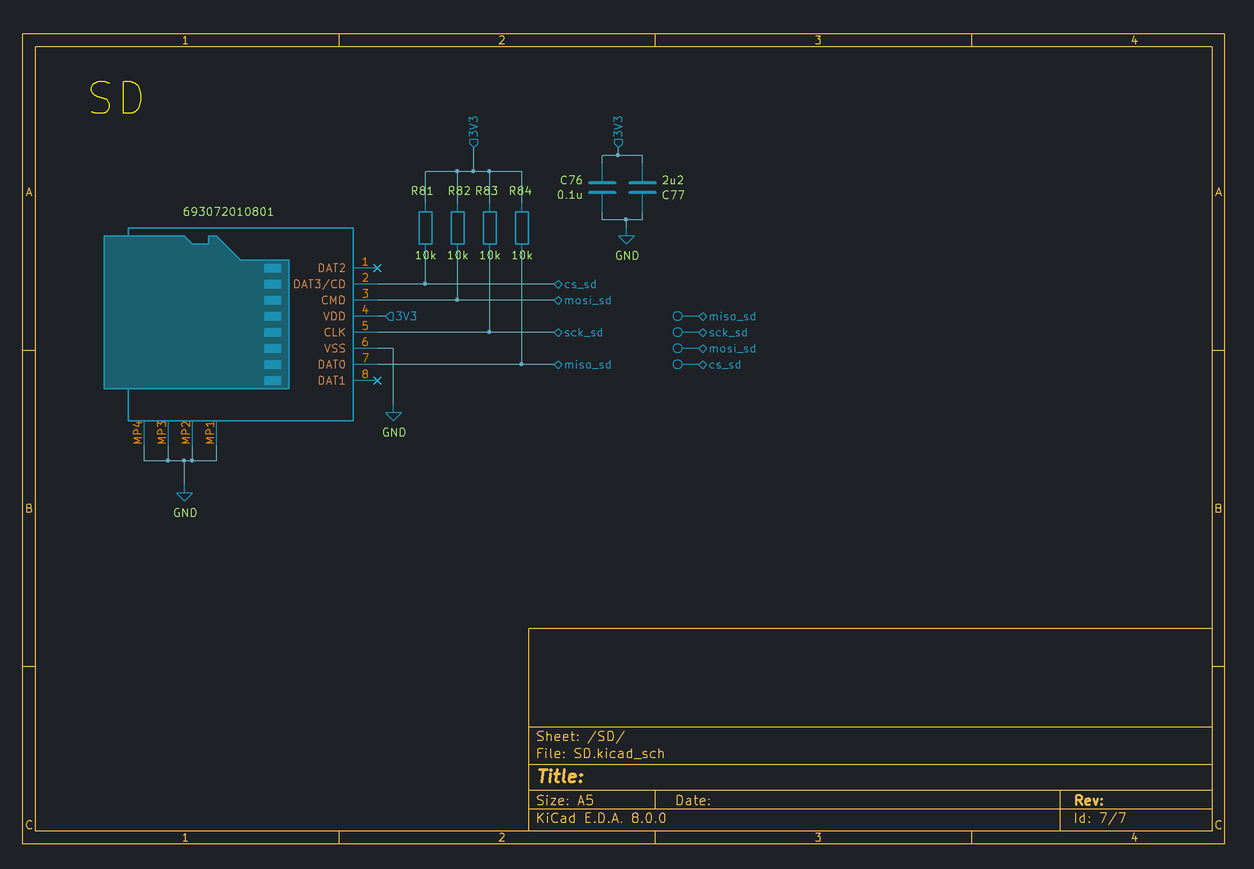
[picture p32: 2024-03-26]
documentation/pictures_for_wiki/ucHardware/pictures/Motherboard_V4_25_3_24-7.png

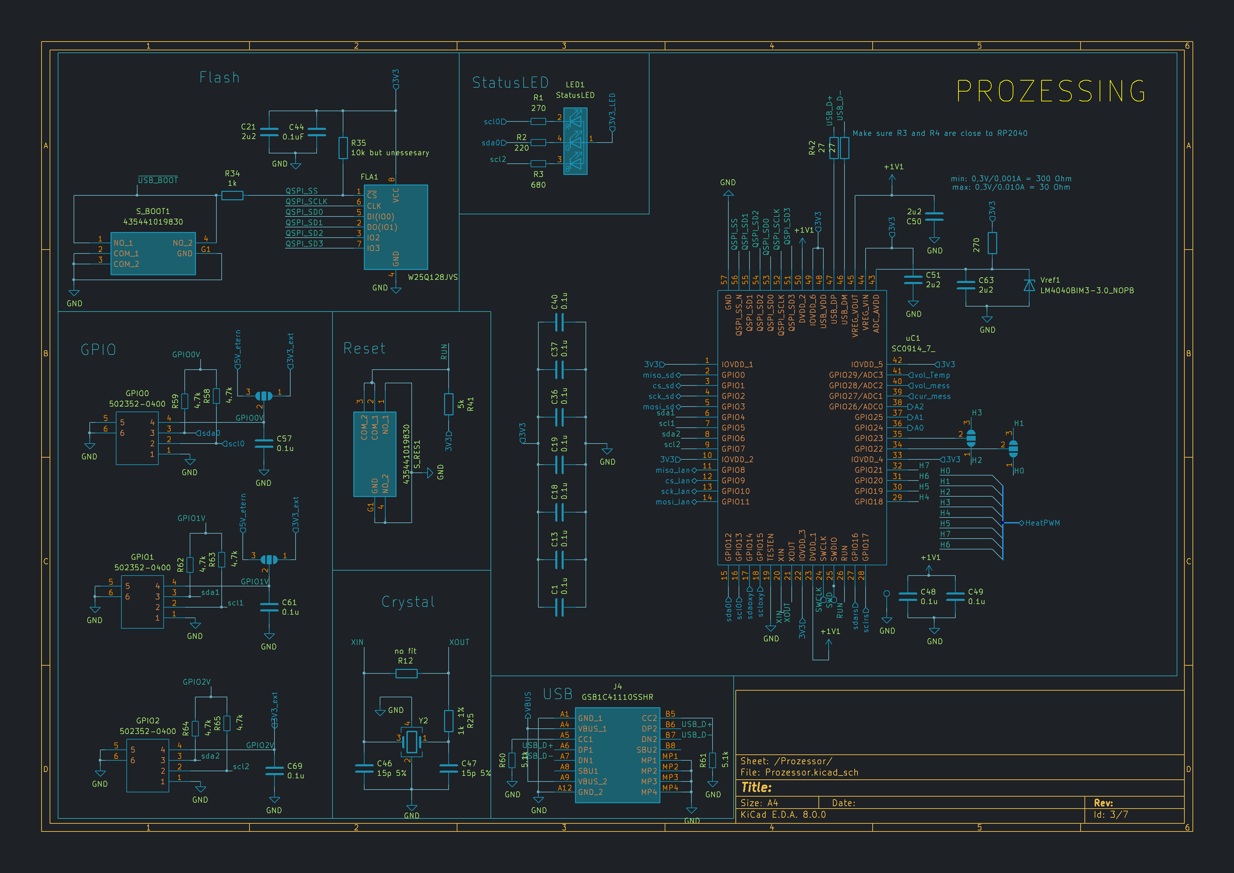
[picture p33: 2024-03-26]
documentation/pictures_for_wiki/ucHardware/pictures/Motherboard_V4_25_3_24-3.png

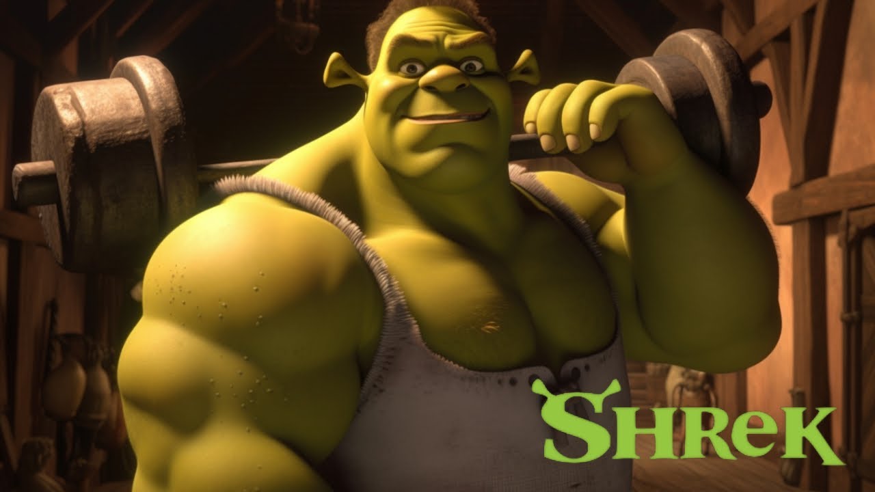
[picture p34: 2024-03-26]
papers/ESA_Symposium_paper/latex/pics/sexyshreksy.jpg

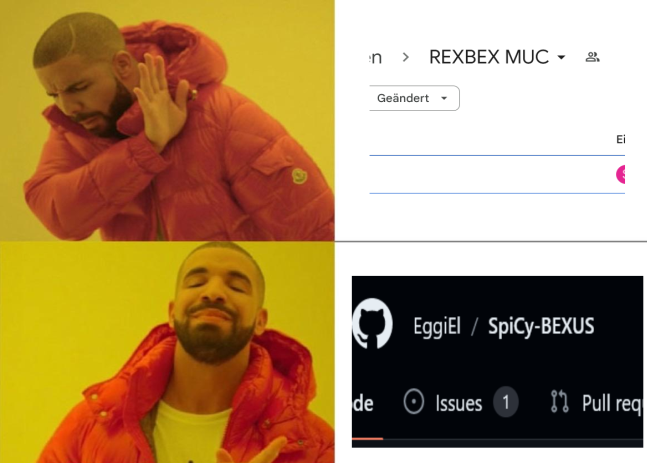
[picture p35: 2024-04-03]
documentation/pictures_for_wiki/ucHardware/pictures/importantNotes.png

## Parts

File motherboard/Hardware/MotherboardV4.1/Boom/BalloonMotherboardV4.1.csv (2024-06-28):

Reference | Qty | Value | Footprint | Mouser Part Number | Datasheet
Y501 | 1 | ECS-250-6-33B2-CTP-TR | SamacSys_Parts:ECS250633B2CTPTR | 520-250-6-33B2-CTPTR | https://ecsxtal.com/products/crystals/surface-mount-crystals/ecs-250-6-33b2-ctp-tr
Y301 | 1 | ABM8G-12.000MHZ-4Y-T3 | SamacSys_Parts:ABM8G | 815-ABM8G-12-4YT3 | ~
V_BAT201 | 1 | 502352-0200 | SamacSys_Parts:5023520200 | 538-502352-0200 | ~
Vref401 | 1 | LM4040BIM3-3.0_NOPB | SamacSys_Parts:SOT95P237X112-3N | 926-LM4040BIM330NOPB | ~
Vref301 | 1 | LM4040BIM3-3.0_NOPB | SamacSys_Parts:SOT95P237X112-3N | 926-LM4040BIM330NOPB | ~
USB_C301 | 1 | GSB1C41110SSHR | SamacSys_Parts:GSB1C41110SSHR |  | https://cdn.amphenol-cs.com/media/wysiwyg/files/drawing/gsb1c41x10sshr-ax1.pdf
uC301 | 1 | SC0914_7_ | QFN40P700X700X90-57N-D | 358-SC09147
U701 | 1 | CD4097B | SOIC127P1030X265-24N |  | http://www.ti.com/lit/ds/symlink/cd4097b.pdf
S_RES301 | 1 | 435441019830 | 435441019830 | 710-435441019830 | https://www.we-online.com/catalog/datasheet/435441019830.pdf
S_BOOT301 | 1 | 435441019830 | 435441019830 | 710-435441019830 | https://www.we-online.com/catalog/datasheet/435441019830.pdf
SD501 | 1 | 693072010801 | SamacSys_Parts:693072010801 | 710-693072010801 | https://www.we-online.de/katalog/datasheet/693072010801.pdf
R_shunt201 | 1 | 10mOhm | Resistor_SMD:R_0805_2012Metric_Pad1.20x1.40mm_HandSolder | 710-580060720008 | https://www.mouser.de/ProductDetail/Wurth-Elektronik/580060720008?qs=unwgFEO1A6tt8z0EuZ69zQ%3D%3D
RT401 | 1 | NTCGS163JF103FT8 | SamacSys_Parts:THRMC1608X90N | 810-NTCGS163JF103FT8 | ~
R701 | 1 | 10k | Resistor_SMD:R_0603_1608Metric_Pad0.98x0.95mm_HandSolder |  | ~
R622 | 1 | 100k | Resistor_SMD:R_0603_1608Metric_Pad0.98x0.95mm_HandSolder |  | ~
R621 | 1 | 100k | Resistor_SMD:R_0603_1608Metric_Pad0.98x0.95mm_HandSolder |  | ~
R620 | 1 | 100 | Resistor_SMD:R_0603_1608Metric_Pad0.98x0.95mm_HandSolder |  | ~
R619 | 1 | 100 | Resistor_SMD:R_0603_1608Metric_Pad0.98x0.95mm_HandSolder |  | ~
R618 | 1 | 100k | Resistor_SMD:R_0603_1608Metric_Pad0.98x0.95mm_HandSolder |  | ~
R617 | 1 | 100k | Resistor_SMD:R_0603_1608Metric_Pad0.98x0.95mm_HandSolder |  | ~
R616 | 1 | 100k | Resistor_SMD:R_0603_1608Metric_Pad0.98x0.95mm_HandSolder |  | ~
R615 | 1 | 100k | Resistor_SMD:R_0603_1608Metric_Pad0.98x0.95mm_HandSolder |  | ~
R614 | 1 | 100k | Resistor_SMD:R_0603_1608Metric_Pad0.98x0.95mm_HandSolder |  | ~
R613 | 1 | 100 | Resistor_SMD:R_0603_1608Metric_Pad0.98x0.95mm_HandSolder |  | ~
R612 | 1 | 100k | Resistor_SMD:R_0603_1608Metric_Pad0.98x0.95mm_HandSolder |  | ~
R611 | 1 | 100 | Resistor_SMD:R_0603_1608Metric_Pad0.98x0.95mm_HandSolder |  | ~
R610 | 1 | 100 | Resistor_SMD:R_0603_1608Metric_Pad0.98x0.95mm_HandSolder |  | ~
R609 | 1 | 100 | Resistor_SMD:R_0603_1608Metric_Pad0.98x0.95mm_HandSolder |  | ~
R608 | 1 | 100 | Resistor_SMD:R_0603_1608Metric_Pad0.98x0.95mm_HandSolder |  | ~
R607 | 1 | 100 | Resistor_SMD:R_0603_1608Metric_Pad0.98x0.95mm_HandSolder |  | ~
R605 | 1 | 10k | Resistor_SMD:R_0603_1608Metric_Pad0.98x0.95mm_HandSolder |  | ~
R604 | 1 | DNP | Resistor_SMD:R_0603_1608Metric_Pad0.98x0.95mm_HandSolder |  | ~
R602 | 1 | 64.9k | Resistor_SMD:R_0603_1608Metric_Pad0.98x0.95mm_HandSolder |  | ~
R601 | 1 | 0 | Resistor_SMD:R_0603_1608Metric_Pad0.98x0.95mm_HandSolder |  | ~
R518 | 1 | 49R9 1% | Resistor_SMD:R_0603_1608Metric_Pad0.98x0.95mm_HandSolder |  | ~
R517 | 1 | 49R9 1% | Resistor_SMD:R_0603_1608Metric_Pad0.98x0.95mm_HandSolder |  | ~
R516 | 1 | 0R | Resistor_SMD:R_0603_1608Metric_Pad0.98x0.95mm_HandSolder |  | ~
R515 | 1 | 0R | Resistor_SMD:R_0603_1608Metric_Pad0.98x0.95mm_HandSolder |  | ~
R514 | 1 | 330 | Resistor_SMD:R_0603_1608Metric_Pad0.98x0.95mm_HandSolder |  | ~
R513 | 1 | 0R | Resistor_SMD:R_0603_1608Metric_Pad0.98x0.95mm_HandSolder |  | ~
R512 | 1 | 12.4k 1% | Resistor_SMD:R_0603_1608Metric_Pad0.98x0.95mm_HandSolder |  | ~
R511 | 1 | 330 | Resistor_SMD:R_0603_1608Metric_Pad0.98x0.95mm_HandSolder |  | ~
R510 | 1 | 10R 1% | Resistor_SMD:R_0603_1608Metric_Pad0.98x0.95mm_HandSolder |  | ~
R509 | 1 | 49R9 1% | Resistor_SMD:R_0603_1608Metric_Pad0.98x0.95mm_HandSolder |  | ~
R508 | 1 | 49R9 1% | Resistor_SMD:R_0603_1608Metric_Pad0.98x0.95mm_HandSolder |  | ~
R507 | 1 | 0R | Resistor_SMD:R_0603_1608Metric_Pad0.98x0.95mm_HandSolder |  | ~
R506 | 1 | 0R | Resistor_SMD:R_0603_1608Metric_Pad0.98x0.95mm_HandSolder |  | ~
R505 | 1 | 1M | Resistor_SMD:R_0603_1608Metric_Pad0.98x0.95mm_HandSolder |  | ~
R504 | 1 | 10k | Resistor_SMD:R_0603_1608Metric_Pad0.98x0.95mm_HandSolder |  | ~
R503 | 1 | 10k | Resistor_SMD:R_0603_1608Metric_Pad0.98x0.95mm_HandSolder |  | ~
R502 | 1 | 10k | Resistor_SMD:R_0603_1608Metric_Pad0.98x0.95mm_HandSolder |  | ~
R501 | 1 | 10k | Resistor_SMD:R_0603_1608Metric_Pad0.98x0.95mm_HandSolder |  | ~
R416 | 1 | 1k | Resistor_SMD:R_0603_1608Metric_Pad0.98x0.95mm_HandSolder |  | ~
R415 | 1 | 1k | Resistor_SMD:R_0603_1608Metric_Pad0.98x0.95mm_HandSolder |  | ~
R414 | 1 | 1k | Resistor_SMD:R_0603_1608Metric_Pad0.98x0.95mm_HandSolder |  | ~
R413 | 1 | 10k | Resistor_SMD:R_0603_1608Metric_Pad0.98x0.95mm_HandSolder |  | ~
R412 | 1 | 270 | Resistor_SMD:R_0603_1608Metric_Pad0.98x0.95mm_HandSolder |  | ~
R411 | 1 | 10k | Resistor_SMD:R_0603_1608Metric_Pad0.98x0.95mm_HandSolder |  | ~
R410 | 1 | 51k | Resistor_SMD:R_0603_1608Metric_Pad0.98x0.95mm_HandSolder |  | ~
R409 | 1 | 5.1k | Resistor_SMD:R_0603_1608Metric_Pad0.98x0.95mm_HandSolder |  | ~
R408 | 1 | 5.1k | Resistor_SMD:R_0603_1608Metric_Pad0.98x0.95mm_HandSolder |  | ~
R407 | 1 | 5.1k | Resistor_SMD:R_0603_1608Metric_Pad0.98x0.95mm_HandSolder |  | ~
R406 | 1 | 5.1k | Resistor_SMD:R_0603_1608Metric_Pad0.98x0.95mm_HandSolder |  | ~
R405 | 1 | 5.1k | Resistor_SMD:R_0603_1608Metric_Pad0.98x0.95mm_HandSolder |  | ~
R404 | 1 | 5.1k | Resistor_SMD:R_0603_1608Metric_Pad0.98x0.95mm_HandSolder |  | ~
R403 | 1 | 5.1k | Resistor_SMD:R_0603_1608Metric_Pad0.98x0.95mm_HandSolder |  | ~
R402 | 1 | 5.1k | Resistor_SMD:R_0603_1608Metric_Pad0.98x0.95mm_HandSolder |  | ~
R401 | 1 | 10k | Resistor_SMD:R_0603_1608Metric_Pad0.98x0.95mm_HandSolder |  | ~
R314 | 1 | 5.1k | Resistor_SMD:R_0603_1608Metric_Pad0.98x0.95mm_HandSolder |  | ~
R313 | 1 | 5.1k | Resistor_SMD:R_0603_1608Metric_Pad0.98x0.95mm_HandSolder |  | ~
R312 | 1 | 1k 1% | Resistor_SMD:R_0603_1608Metric_Pad0.98x0.95mm_HandSolder |  | ~
R311 | 1 | no fit | Resistor_SMD:R_0402_1005Metric_Pad0.72x0.64mm_HandSolder |  | ~
R310 | 1 | 4.7k | Resistor_SMD:R_0603_1608Metric_Pad0.98x0.95mm_HandSolder |  | ~
R309 | 1 | 4.7k | Resistor_SMD:R_0603_1608Metric_Pad0.98x0.95mm_HandSolder |  | ~
R308 | 1 | 4.7k | Resistor_SMD:R_0603_1608Metric_Pad0.98x0.95mm_HandSolder |  | ~
R307 | 1 | 4.7k | Resistor_SMD:R_0603_1608Metric_Pad0.98x0.95mm_HandSolder |  | ~
R306 | 1 | 5.1k | Resistor_SMD:R_0603_1608Metric_Pad0.98x0.95mm_HandSolder |  | ~
R305 | 1 | 150 | Resistor_SMD:R_0603_1608Metric_Pad0.98x0.95mm_HandSolder |  | ~
R304 | 1 | 1k | Resistor_SMD:R_0603_1608Metric_Pad0.98x0.95mm_HandSolder |  | ~
R303 | 1 | 27 | Resistor_SMD:R_0603_1608Metric_Pad0.98x0.95mm_HandSolder |  | ~
R302 | 1 | 27 | Resistor_SMD:R_0603_1608Metric_Pad0.98x0.95mm_HandSolder |  | ~
R301 | 1 | 10k but unessesary | Resistor_SMD:R_0603_1608Metric_Pad0.98x0.95mm_HandSolder |  | ~
R208 | 1 | 10k | Resistor_SMD:R_0603_1608Metric_Pad0.98x0.95mm_HandSolder |  | ~
R207 | 1 | 100k | Resistor_SMD:R_0603_1608Metric_Pad0.98x0.95mm_HandSolder |  | ~
R206 | 1 | 500 | Resistor_SMD:R_0603_1608Metric_Pad0.98x0.95mm_HandSolder |  | ~
R205 | 1 | 12k | Resistor_SMD:R_0603_1608Metric_Pad0.98x0.95mm_HandSolder |  | ~
R204 | 1 | 10k | Resistor_SMD:R_0603_1608Metric_Pad0.98x0.95mm_HandSolder |  | ~
R203 | 1 | DNP | Resistor_SMD:R_0603_1608Metric_Pad0.98x0.95mm_HandSolder |  | ~
R202 | 1 | 64.9k | Resistor_SMD:R_0603_1608Metric_Pad0.98x0.95mm_HandSolder |  | ~
R201 | 1 | 0 | Resistor_SMD:R_0603_1608Metric_Pad0.98x0.95mm_HandSolder |  | ~
R0 | 1 | 500 | Resistor_SMD:R_0603_1608Metric_Pad0.98x0.95mm_HandSolder |  | ~
Q608 | 1 | IRLML6344TRPBF | SOT95P237X112-3N | 942-IRLML6344TRPBF | https://www.infineon.com/dgdl/irlml6344pbf.pdf?fileId=5546d462533600a4015356689c44262c
Q607 | 1 | IRLML6344TRPBF | SOT95P237X112-3N | 942-IRLML6344TRPBF | https://www.infineon.com/dgdl/irlml6344pbf.pdf?fileId=5546d462533600a4015356689c44262c
Q606 | 1 | IRLML6344TRPBF | SOT95P237X112-3N | 942-IRLML6344TRPBF | https://www.infineon.com/dgdl/irlml6344pbf.pdf?fileId=5546d462533600a4015356689c44262c
Q605 | 1 | IRLML6344TRPBF | SOT95P237X112-3N | 942-IRLML6344TRPBF | https://www.infineon.com/dgdl/irlml6344pbf.pdf?fileId=5546d462533600a4015356689c44262c
Q604 | 1 | IRLML6344TRPBF | SOT95P237X112-3N | 942-IRLML6344TRPBF | https://www.infineon.com/dgdl/irlml6344pbf.pdf?fileId=5546d462533600a4015356689c44262c
Q603 | 1 | IRLML6344TRPBF | SOT95P237X112-3N | 942-IRLML6344TRPBF | https://www.infineon.com/dgdl/irlml6344pbf.pdf?fileId=5546d462533600a4015356689c44262c
Q602 | 1 | IRLML6344TRPBF | SOT95P237X112-3N | 942-IRLML6344TRPBF | https://www.infineon.com/dgdl/irlml6344pbf.pdf?fileId=5546d462533600a4015356689c44262c
Q601 | 1 | IRLML6344TRPBF | SOT95P237X112-3N | 942-IRLML6344TRPBF | https://www.infineon.com/dgdl/irlml6344pbf.pdf?fileId=5546d462533600a4015356689c44262c
OP401 | 1 | TLV9002QDRQ1 | SamacSys_Parts:SOIC127P600X175-8N |  | ~
NTC406 | 1 | 502352-0200 | SamacSys_Parts:5023520200 | 538-502352-0200 | ~
NTC405 | 1 | 502352-0200 | SamacSys_Parts:5023520200 | 538-502352-0200 | ~
NTC404 | 1 | 502352-0200 | SamacSys_Parts:5023520200 | 538-502352-0200 | ~
NTC403 | 1 | 502352-0200 | SamacSys_Parts:5023520200 | 538-502352-0200 | ~
NTC402 | 1 | 502352-0200 | SamacSys_Parts:5023520200 | 538-502352-0200 | ~
NTC401 | 1 | 502352-0200 | SamacSys_Parts:5023520200 | 538-502352-0200 | ~
MUX401 | 1 | TMUX1108PWR | SOP65P640X120-16N | 595-TMUX1108PWR | http://www.ti.com/lit/ds/symlink/tmux1108.pdf
LRuC201 | 1 | NCP1117ST33T3G | SamacSys_Parts:SOT230P700X180-4N | 863-NCP1117ST33T3G | http://www.onsemi.com/pub/Collateral/NCP1117-D.PDF
LRre201 | 1 | NCP1117ST33T3G | SamacSys_Parts:SOT230P700X180-4N | 863-NCP1117ST33T3G | http://www.onsemi.com/pub/Collateral/NCP1117-D.PDF
LRlan201 | 1 | NCP1117ST33T3G | SamacSys_Parts:SOT230P700X180-4N | 863-NCP1117ST33T3G | http://www.onsemi.com/pub/Collateral/NCP1117-D.PDF
LAN501 | 1 | W5500 | SamacSys_Parts:QFP50P900X900X160-48N | 950-W5500 | http://wizwiki.net/wiki/lib/exe/fetch.php?media=products:w5500:w5500_ds_v106e_141230.pdf
L601 | 1 | 74439346068 | SamacSys_Parts:74439346068 | 710-74439346068 | ~
L201 | 1 | 74439346068 | SamacSys_Parts:74439346068 | 710-74439346068 | ~
JB_or_U201 | 1 | Conn_01x03 | Connector_PinHeader_2.54mm:PinHeader_1x03_P2.54mm_Vertical |  | ~
J706 | 1 | 502352-0400 | 5023520400 | 538-502352-0400 | https://www.molex.com/webdocs/datasheets/pdf/en-us/5023520400_PCB_HEADERS.pdf
J705 | 1 | 502352-0400 | 5023520400 | 538-502352-0400 | https://www.molex.com/webdocs/datasheets/pdf/en-us/5023520400_PCB_HEADERS.pdf
J704 | 1 | 502352-0400 | 5023520400 | 538-502352-0400 | https://www.molex.com/webdocs/datasheets/pdf/en-us/5023520400_PCB_HEADERS.pdf
J703 | 1 | 502352-0400 | 5023520400 | 538-502352-0400 | https://www.molex.com/webdocs/datasheets/pdf/en-us/5023520400_PCB_HEADERS.pdf
J702 | 1 | 502352-0400 | 5023520400 | 538-502352-0400 | https://www.molex.com/webdocs/datasheets/pdf/en-us/5023520400_PCB_HEADERS.pdf
J701 | 1 | 502352-0400 | 5023520400 | 538-502352-0400 | https://www.molex.com/webdocs/datasheets/pdf/en-us/5023520400_PCB_HEADERS.pdf
J501 | 1 | J1B1211CCD | SamacSys_Parts:J1B1211CCD | 950-J1B1211CCD | http://wizwiki.net/wiki/lib/exe/fetch.php?media=products:wiz550web:wiz550webds_kr:j1b1211ccd.pdf
J401 | 1 | 0 | Resistor_SMD:R_0603_1608Metric_Pad0.98x0.95mm_HandSolder |  | ~
J201 | 1 | 0 | Resistor_SMD:R_0603_1608Metric_Pad0.98x0.95mm_HandSolder |  | ~
J0 | 1 | 0 | Resistor_SMD:R_0603_1608Metric_Pad0.98x0.95mm_HandSolder |  | ~
IC201 | 1 | INA240A3EDRQ1 | SOIC127P600X175-8N | 595-INA240A3EDRQ1 | http://www.ti.com/lit/gpn/INA240-Q1
HEAT_CON608 | 1 | 502352-0200 | SamacSys_Parts:5023520200 | 538-502352-0200 | ~
HEAT_CON607 | 1 | 502352-0200 | SamacSys_Parts:5023520200 | 538-502352-0200 | ~
HEAT_CON606 | 1 | 502352-0200 | SamacSys_Parts:5023520200 | 538-502352-0200 | ~
HEAT_CON605 | 1 | 502352-0200 | SamacSys_Parts:5023520200 | 538-502352-0200 | ~
HEAT_CON604 | 1 | 502352-0200 | SamacSys_Parts:5023520200 | 538-502352-0200 | ~
HEAT_CON603 | 1 | 502352-0200 | SamacSys_Parts:5023520200 | 538-502352-0200 | ~
HEAT_CON602 | 1 | 502352-0200 | SamacSys_Parts:5023520200 | 538-502352-0200 | ~
HEAT_CON601 | 1 | 502352-0200 | SamacSys_Parts:5023520200 | 538-502352-0200 | ~
H3_M101 | 1 | MountingHole | MountingHole:MountingHole_3.2mm_M3_Pad_Via |  | ~
H2_M102 | 1 | MountingHole | MountingHole:MountingHole_3.2mm_M3_Pad_Via |  | ~
H2_M101 | 1 | MountingHole | MountingHole:MountingHole_3.2mm_M3_Pad_Via |  | ~
H0_M101 | 1 | MountingHole | MountingHole:MountingHole_3.2mm_M3_Pad_Via |  | ~
GPIO302 | 1 | 502352-0400 | SamacSys_Parts:5023520400 | 538-502352-0400 | https://www.molex.com/webdocs/datasheets/pdf/en-us/5023520400_PCB_HEADERS.pdf
GPIO301 | 1 | 502352-0400 | SamacSys_Parts:5023520400 | 538-502352-0400 | https://www.molex.com/webdocs/datasheets/pdf/en-us/5023520400_PCB_HEADERS.pdf
FLA301 | 1 | W25Q128JVS | SamacSys_Parts:SOIC127P790X216-8N |  | http://www.winbond.com/resource-files/w25q128jv_dtr%20revc%2003272018%20plus.pdf
FB501 | 1 | BLM18SP102SZ1D | SamacSys_Parts:BLM18SP221SN1B | 81-BLM18SP102SZ1D | ~
F608 | 1 | MF-FSML100_8-2 | SamacSys_Parts:FUSC1608X70N | 652-MF-FSML100/8-2 | ~
F607 | 1 | MF-FSML100_8-2 | SamacSys_Parts:FUSC1608X70N | 652-MF-FSML100/8-2 | ~
F606 | 1 | MF-FSML100_8-2 | SamacSys_Parts:FUSC1608X70N | 652-MF-FSML100/8-2 | ~
F605 | 1 | MF-FSML100_8-2 | SamacSys_Parts:FUSC1608X70N | 652-MF-FSML100/8-2 | ~
F604 | 1 | MF-FSML100_8-2 | SamacSys_Parts:FUSC1608X70N | 652-MF-FSML100/8-2 | ~
F603 | 1 | MF-FSML100_8-2 | SamacSys_Parts:FUSC1608X70N | 652-MF-FSML100/8-2 | ~
F602 | 1 | MF-FSML100_8-2 | SamacSys_Parts:FUSC1608X70N | 652-MF-FSML100/8-2 | ~
F601 | 1 | MF-FSML100_8-2 | SamacSys_Parts:FUSC1608X70N | 652-MF-FSML100/8-2 | ~
D203 | 1 | RBR2LB60BTBR1 | SamacSys_Parts:DIOM5336X245N | 755-RBR2LB60BTBR1 | ~
D202 | 1 | RBR2LB60BTBR1 | SamacSys_Parts:DIOM5336X245N | 755-RBR2LB60BTBR1 | ~
D201 | 1 | RBR2LB60BTBR1 | SamacSys_Parts:DIOM5336X245N | 755-RBR2LB60BTBR1 | ~
C613 | 1 | DNP | Capacitor_SMD:C_0805_2012Metric_Pad1.18x1.45mm_HandSolder |  | ~
C612 | 1 | 22u | Capacitor_SMD:C_0805_2012Metric_Pad1.18x1.45mm_HandSolder |  | ~
C611 | 1 | 22u | Capacitor_SMD:C_0805_2012Metric_Pad1.18x1.45mm_HandSolder |  | ~
C610 | 1 | 33n | Capacitor_SMD:C_0805_2012Metric_Pad1.18x1.45mm_HandSolder |  | ~
C609 | 1 | 0.1u/30V | Capacitor_SMD:C_0402_1005Metric_Pad0.74x0.62mm_HandSolder |  | ~
C608 | 1 | 10u/30V | Capacitor_SMD:C_0805_2012Metric_Pad1.18x1.45mm_HandSolder |  | ~
C607 | 1 | DNP | Capacitor_SMD:C_0805_2012Metric_Pad1.18x1.45mm_HandSolder |  | ~
C606 | 1 | DNP | Capacitor_SMD:C_0805_2012Metric_Pad1.18x1.45mm_HandSolder |  | ~
C605 | 1 | 0.1u/30V DNP | Capacitor_SMD:C_0805_2012Metric_Pad1.18x1.45mm_HandSolder |  | ~
C604 | 1 | 1u/30V DNP | Capacitor_SMD:C_0805_2012Metric_Pad1.18x1.45mm_HandSolder |  | ~
C601 | 1 | 0.1u | Capacitor_SMD:C_0402_1005Metric_Pad0.74x0.62mm_HandSolder |  | ~
C520 | 1 | 10n | Capacitor_SMD:C_0805_2012Metric_Pad1.18x1.45mm_HandSolder |  | ~
C519 | 1 | 4.7u | Capacitor_SMD:C_0805_2012Metric_Pad1.18x1.45mm_HandSolder |  | ~
C518 | 1 | 10n | Capacitor_SMD:C_0805_2012Metric_Pad1.18x1.45mm_HandSolder |  | ~
C517 | 1 | 6.8n | Capacitor_SMD:C_0805_2012Metric_Pad1.18x1.45mm_HandSolder |  | ~
C516 | 1 | 1nF/200V | Capacitor_SMD:C_0805_2012Metric_Pad1.18x1.45mm_HandSolder |  | ~
C515 | 1 | 6.8n | Capacitor_SMD:C_0805_2012Metric_Pad1.18x1.45mm_HandSolder |  | ~
C514 | 1 | 22nF | Capacitor_SMD:C_0805_2012Metric_Pad1.18x1.45mm_HandSolder |  | ~
C513 | 1 | 10uF/16V | Capacitor_SMD:C_0805_2012Metric_Pad1.18x1.45mm_HandSolder |  | ~
C512 | 1 | 0.1u | Capacitor_SMD:C_0402_1005Metric_Pad0.74x0.62mm_HandSolder |  | ~
C511 | 1 | 18p | Capacitor_SMD:C_0402_1005Metric_Pad0.74x0.62mm_HandSolder |  | ~
C510 | 1 | 18p | Capacitor_SMD:C_0402_1005Metric_Pad0.74x0.62mm_HandSolder |  | ~
C509 | 1 | 10uF/16V | Capacitor_SMD:C_0805_2012Metric_Pad1.18x1.45mm_HandSolder |  | ~
C508 | 1 | 0.1u | Capacitor_SMD:C_0402_1005Metric_Pad0.74x0.62mm_HandSolder |  | ~
C507 | 1 | 0.1u | Capacitor_SMD:C_0402_1005Metric_Pad0.74x0.62mm_HandSolder |  | ~
C506 | 1 | 0.1u | Capacitor_SMD:C_0402_1005Metric_Pad0.74x0.62mm_HandSolder |  | ~
C505 | 1 | 0.1u | Capacitor_SMD:C_0402_1005Metric_Pad0.74x0.62mm_HandSolder |  | ~
C504 | 1 | 0.1u | Capacitor_SMD:C_0402_1005Metric_Pad0.74x0.62mm_HandSolder |  | ~
C503 | 1 | 0.1u | Capacitor_SMD:C_0402_1005Metric_Pad0.74x0.62mm_HandSolder |  | ~
C502 | 1 | 0.1u | Capacitor_SMD:C_0402_1005Metric_Pad0.74x0.62mm_HandSolder |  | ~
C501 | 1 | 2u2 | Capacitor_SMD:C_0805_2012Metric_Pad1.18x1.45mm_HandSolder |  | ~
C403 | 1 | 0.1uF | Capacitor_SMD:C_0402_1005Metric_Pad0.74x0.62mm_HandSolder |  | ~
C401 | 1 | 10u | Capacitor_SMD:C_0805_2012Metric_Pad1.18x1.45mm_HandSolder |  | ~
C317 | 1 | 15p 5% | Capacitor_SMD:C_0402_1005Metric_Pad0.74x0.62mm_HandSolder |  | ~
C316 | 1 | 15p 5% | Capacitor_SMD:C_0402_1005Metric_Pad0.74x0.62mm_HandSolder |  | ~
C315 | 1 | 0.1u | Capacitor_SMD:C_0402_1005Metric_Pad0.74x0.62mm_HandSolder |  | ~
C314 | 1 | 0.1u | Capacitor_SMD:C_0402_1005Metric_Pad0.74x0.62mm_HandSolder |  | ~
C313 | 1 | 0.1u | Capacitor_SMD:C_0402_1005Metric_Pad0.74x0.62mm_HandSolder |  | ~
C312 | 1 | 0.1u | Capacitor_SMD:C_0402_1005Metric_Pad0.74x0.62mm_HandSolder |  | ~
C311 | 1 | 0.1u | Capacitor_SMD:C_0402_1005Metric_Pad0.74x0.62mm_HandSolder |  | ~
C310 | 1 | 0.1u | Capacitor_SMD:C_0402_1005Metric_Pad0.74x0.62mm_HandSolder |  | ~
C309 | 1 | 0.1u | Capacitor_SMD:C_0402_1005Metric_Pad0.74x0.62mm_HandSolder |  | ~
C308 | 1 | 2u2 | Capacitor_SMD:C_0805_2012Metric_Pad1.18x1.45mm_HandSolder |  | ~
C307 | 1 | 2u2 | Capacitor_SMD:C_0805_2012Metric_Pad1.18x1.45mm_HandSolder |  | ~
C306 | 1 | 0.1u | Capacitor_SMD:C_0402_1005Metric_Pad0.74x0.62mm_HandSolder |  | ~
C305 | 1 | 0.1u | Capacitor_SMD:C_0402_1005Metric_Pad0.74x0.62mm_HandSolder |  | ~
C304 | 1 | 2u2 | Capacitor_SMD:C_0805_2012Metric_Pad1.18x1.45mm_HandSolder |  | ~
C303 | 1 | 0.1u | Capacitor_SMD:C_0402_1005Metric_Pad0.74x0.62mm_HandSolder |  | ~
C302 | 1 | 0.1uF | Capacitor_SMD:C_0402_1005Metric_Pad0.74x0.62mm_HandSolder |  | ~
C301 | 1 | 2u2 | Capacitor_SMD:C_0805_2012Metric_Pad1.18x1.45mm_HandSolder |  | ~
C217 | 1 | 10u | Capacitor_SMD:C_0805_2012Metric_Pad1.18x1.45mm_HandSolder |  | ~
C216 | 1 | 10u | Capacitor_SMD:C_0805_2012Metric_Pad1.18x1.45mm_HandSolder |  | ~
C215 | 1 | 0.1u | Capacitor_SMD:C_0402_1005Metric_Pad0.74x0.62mm_HandSolder |  | ~
C214 | 1 | 10u | Capacitor_SMD:C_0805_2012Metric_Pad1.18x1.45mm_HandSolder |  | ~
C213 | 1 | 10u | Capacitor_SMD:C_0805_2012Metric_Pad1.18x1.45mm_HandSolder |  | ~
C212 | 1 | DNP | Capacitor_SMD:C_0805_2012Metric_Pad1.18x1.45mm_HandSolder |  | ~
C211 | 1 | 22u | Capacitor_SMD:C_0805_2012Metric_Pad1.18x1.45mm_HandSolder |  | ~
C210 | 1 | 22u | Capacitor_SMD:C_0805_2012Metric_Pad1.18x1.45mm_HandSolder |  | ~
C209 | 1 | 33n | Capacitor_SMD:C_0805_2012Metric_Pad1.18x1.45mm_HandSolder |  | ~
C207 | 1 | 0.1u/30V | Capacitor_SMD:C_0402_1005Metric_Pad0.74x0.62mm_HandSolder |  | ~
C206 | 1 | DNP | Capacitor_SMD:C_0805_2012Metric_Pad1.18x1.45mm_HandSolder |  | ~
C205 | 1 | DNP | Capacitor_SMD:C_0805_2012Metric_Pad1.18x1.45mm_HandSolder |  | ~
C204 | 1 | 10u/30V | Capacitor_SMD:C_0805_2012Metric_Pad1.18x1.45mm_HandSolder |  | ~
C203 | 1 | 10u | Capacitor_SMD:C_0805_2012Metric_Pad1.18x1.45mm_HandSolder |  | ~
C202 | 1 | 10u | Capacitor_SMD:C_0805_2012Metric_Pad1.18x1.45mm_HandSolder |  | ~
C201 | 1 | 0.1u | Capacitor_SMD:C_0402_1005Metric_Pad0.74x0.62mm_HandSolder |  | ~
BuckJmp601 | 1 | Conn_01x03 | Connector_PinHeader_2.54mm:PinHeader_1x03_P2.54mm_Vertical |  | ~
BuckJmp201 | 1 | Conn_01x03 | Connector_PinHeader_2.54mm:PinHeader_1x03_P2.54mm_Vertical |  | ~
BUCK601 | 1 | TPS62933DRLR | SamacSys_Parts:SOTFL50P160X60-8N | 595-TPS62933DRLR | https://www.ti.com/lit/ds/symlink/tps62933.pdf?ts=1626073394234
BUCK201 | 1 | TPS62933DRLR | SamacSys_Parts:SOTFL50P160X60-8N | 595-TPS62933DRLR | https://www.ti.com/lit/ds/symlink/tps62933.pdf?ts=1626073394234
bat201 | 1 | APTD2012LSURCK | SamacSys_Parts:LEDM2012X120N | 604-APTD2012LSURCK | ~
5sys201 | 1 | APTD2012LCGCK | SamacSys_Parts:LEDC2012X120N | 604-APTD2012LCGCK | ~
5sys0 | 1 | APTD2012LCGCK | SamacSys_Parts:LEDC2012X120N | 604-APTD2012LCGCK | ~

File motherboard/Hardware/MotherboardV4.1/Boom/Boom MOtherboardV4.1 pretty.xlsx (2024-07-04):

Reference | Qty | Value | Footprint (imperial) | Mouser Part Number | Datasheet
5sys0 | 2 | APTD2012LCGCK | LEDC2012X120N | 604-APTD2012LCGCK | ~
bat201 | 1 | APTD2012LSURCK | LEDM2012X120N | 604-APTD2012LSURCK | ~
BUCK201 | 2 | TPS62933DRLR | SOTFL50P160X60-8N | 595-TPS62933DRLR | https://www.ti.com/lit/ds/symlink/tps62933.pdf?ts=1626073394234
BuckJmp201 | 3 | Conn_01x03 | PinHeader_1x03_P2.54mm_Vertical |  | ~
C201 | 24 | 0.1u | 402 | 80-C0402C104K4R7411 | ~
 |  |  |  |  | ~
C204 | 2 | 10u/30V | 805 | 81-GRM21BC8YA106ME1L | ~
C207 | 2 | 0.1u/30V | 402 | 81-GRM155R62A104ME4D | ~
C209 | 2 | 33n | 805 | 710-88501220706 | ~
C210 | 4 | 22u | 805 | 187-CL21A226MAYNNNE | ~
C301 | 5 | 2u2 | 805 | 187-CL21A225KOFNNNE | ~
C316 | 2 | 15p 5% | 402 | 710-885012005008 | ~
C509 | 9 | 10uF/16V | 805 | 187-CL21A106KOQNNNF | ~
C510 | 2 | 18p | 402 | 81-GRM1555C1H180JA1J | ~
C514 | 1 | 22nF | 805 | 710-885012207041 | ~
C515 | 2 | 6.8n | 805 | 710-885012207121 | ~
C516 | 1 | 1nF/200V | 805 | 791-0805N150J201CT | ~
C518 | 2 | 10n | 805 | 710-885012207039 | ~
D201 | 3 | RBR2LB60BTBR1 | DIOM5336X245N | 755-RBR2LB60BTBR1 | ~
F601 | 8 | MF-FSML100_8-2 | FUSC1608X70N | 652-MF-FSML100/8-2 | ~
FB501 | 1 | BLM18SP102SZ1D | BLM18SP221SN1B | 81-BLM18SP102SZ1D | ~
FLA301 | 1 | W25Q128JVS | SOIC127P790X216-8N | 454-W25Q128JVSIMTR | http://www.winbond.com/resource-files/w25q128jv_dtr%20revc%2003272018%20plus.pdf
HEAT_CON601 | 15 | 502352-0200 | 5023520200 | 538-502352-0200 | ~
IC201 | 1 | INA240A3EDRQ1 | SOIC127P600X175-8N | 595-INA240A3EDRQ1 | http://www.ti.com/lit/gpn/INA240-Q1
J501 | 1 | J1B1211CCD | J1B1211CCD | 950-J1B1211CCD | http://wizwiki.net/wiki/lib/exe/fetch.php?media=products:wiz550web:wiz550webds_kr:j1b1211ccd.pdf
J701 | 7 | 502352-0400 | 5023520400 | 538-502352-0400 | https://www.molex.com/webdocs/datasheets/pdf/en-us/5023520400_PCB_HEADERS.pdf
L201 | 2 | 74439346068 | 74439346068 | 710-74439346068 | ~
LAN501 | 1 | W5500 | QFP50P900X900X160-48N | 950-W5500 | http://wizwiki.net/wiki/lib/exe/fetch.php?media=products:w5500:w5500_ds_v106e_141230.pdf
LRlan201 | 2 | NCP1117ST33T3G | SOT230P700X180-4N | 863-NCP1117ST33T3G | http://www.onsemi.com/pub/Collateral/NCP1117-D.PDF
LRuC201 | 1 | NCP1117ST33T3G | SOT230P700X180-4N | 863-NCP1117ST33T3G | http://www.onsemi.com/pub/Collateral/NCP1117-D.PDF
MUX401 | 1 | TMUX1108PWR | SOP65P640X120-16N | 595-TMUX1108PWR | http://www.ti.com/lit/ds/symlink/tmux1108.pdf
OP401 | 1 | TLV9002QDRQ1 | SOIC127P600X175-8N | 595-TLV9002QDRQ1 | ~
Q601 | 8 | IRLML6344TRPBF | SOT95P237X112-3N | 942-IRLML6344TRPBF | https://www.infineon.com/dgdl/irlml6344pbf.pdf?fileId=5546d462533600a4015356689c44262c
R_shunt201 | 1 | 10mOhm | 805 | 710-580060720008 | https://www.mouser.de/ProductDetail/Wurth-Elektronik/580060720008?qs=unwgFEO1A6tt8z0EuZ69zQ%3D%3D
R0 | 2 | 500 | 603 |  | ~
R202 | 2 | 64.9k | 603 |  | ~
R204 | 10 | 10k | 603 |  | ~
R205 | 1 | 12k | 603 |  | ~
R207 | 9 | 100k | 603 |  | ~
R302 | 2 | 27 | 603 |  | ~
R305 | 1 | 150 | 603 |  | ~
R306 | 11 | 5.1k 1% | 603 |  | ~
R307 | 5 | 4.7k | 603 |  | ~
R312 | 5 | 1k 1% | 603 |  | ~
R410 | 1 | 51k 1% | 603 |  | ~
R412 | 1 | 270 | 603 |  | ~
R505 | 1 | 1M | 603 |  | ~
R506 | 10 | 0R | 603 |  | ~
R508 | 4 | 49R9 1% | 603 |  | ~
R510 | 1 | 10R 1% | 603 |  | ~
R511 | 2 | 330 | 603 |  | ~
R512 | 1 | 12.4k 1% | 603 |  | ~
R607 | 8 | 100 | 603 |  | ~
RT401 | 1 | NTCGS163JF103FT8 | THRMC1608X90N | 810-NTCGS163JF103FT8 | ~
S_BOOT301 | 2 | 435441019830 | 435441019830 | 710-435441019830 | https://www.we-online.com/catalog/datasheet/435441019830.pdf
SD501 | 1 | 693072010801 | 693072010801 | 710-693072010801 | https://www.we-online.de/katalog/datasheet/693072010801.pdf
U701 | 1 | CD4097B | SOIC127P1030X265-24N | 595-CD4097BM | http://www.ti.com/lit/ds/symlink/cd4097b.pdf
uC301 | 1 | SC0914_7_ | QFN40P700X700X90-57N-D | 358-SC09147
USB_C301 | 1 | GSB1C41110SSHR | GSB1C41110SSHR | 523-GSB1C41110SSHR | https://cdn.amphenol-cs.com/media/wysiwyg/files/drawing/gsb1c41x10sshr-ax1.pdf
Vref301 | 2 | LM4040BIM3-3.0_NOPB | SOT95P237X112-3N | 926-LM4040BIM330NOPB | ~
Y301 | 1 | ABM8G-12.000MHZ-4Y-T3 | ABM8G | 815-ABM8G-12-4YT3 | ~
Y501 | 1 | ECS-250-6-33B2-CTP-TR | ECS250633B2CTPTR | 520-250-6-33B2-CTPTR | https://ecsxtal.com/products/crystals/surface-mount-crystals/ecs-250-6-33b2-ctp-tr
Cabeling | HUGE
Banana Plug | 2
Ethernet Plug | 1

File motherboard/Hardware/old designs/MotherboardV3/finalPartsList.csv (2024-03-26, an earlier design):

Column1 | Value | Cmp name | Footprint | Description | Vendor | DNP
C28, C30, C32, C33, C34, C35, C42 | 7 | 0.1uF | C | Capacitor_SMD:C_0402_1005Metric | Unpolarized capacitor
C18, C19, C40, C41, C44, C46, C47, C48, C49, C50, C51 | 11 | 100n | C | Capacitor_SMD:C_0402_1005Metric | Unpolarized capacitor
C54, C55, C56, C57, C58, C59, C60, C61 | 8 | 200nF | C | Capacitor_SMD:C_0402_1005Metric | Unpolarized capacitor
C10 | 1 | 1nF/200V | C | Capacitor_SMD:C_0402_1005Metric | Unpolarized capacitor
C1, C13 | 2 | 1u | C | Capacitor_SMD:C_0402_1005Metric | Unpolarized capacitor
C12, C24 | 2 | 0.1u | C | Capacitor_SMD:C_0402_1005Metric | Unpolarized capacitor
C15, C16 | 2 | 18p | C | Capacitor_SMD:C_0402_1005Metric | Unpolarized capacitor
C29, C53 | 2 | 10nF | C | Capacitor_SMD:C_0402_1005Metric | Unpolarized capacitor
C36, C37 | 2 | 15p | C | Capacitor_SMD:C_0402_1005Metric | Unpolarized capacitor
C45, C52 | 2 | 6.8nF | C | Capacitor_SMD:C_0402_1005Metric | Unpolarized capacitor
C9 | 1 | 22nF | C | Capacitor_SMD:C_0402_1005Metric | Unpolarized capacitor
C11, C14, C17, C22 | 4 | 100nF | C | Capacitor_SMD:C_0603_1608Metric | Unpolarized capacitor
C25 | 1 | 0.1uF | C | Capacitor_SMD:C_0603_1608Metric | Unpolarized capacitor
C23 | 1 | 0.22uF | C | Capacitor_SMD:C_0603_1608Metric | Unpolarized capacitor
C2, C7 | 2 | 0.47uF | C | Capacitor_SMD:C_0603_1608Metric | Unpolarized capacitor
C4, C8 | 2 | 33uF | C | Capacitor_SMD:C_0603_1608Metric | Unpolarized capacitor
C20, C21 | 2 | 22uF | C | Capacitor_SMD:C_0603_1608Metric | Unpolarized capacitor
C3 | 1 | 33nF | C | Capacitor_SMD:C_0603_1608Metric | Unpolarized capacitor
C26 | 1 | 1u | C | Capacitor_SMD:C_0805_2012Metric | Unpolarized capacitor
C38, C39 | 2 | 10u | C | Capacitor_SMD:C_0805_2012Metric | Unpolarized capacitor
C5, C6 | 2 | 10uF | C | Capacitor_SMD:C_1206_3216Metric_Pad1.33x1.80mm_HandSolder | Unpolarized capacitor
C27, C43 | 2 | 10uF/16V | C | Capacitor_SMD:C_1206_3216Metric_Pad1.33x1.80mm_HandSolder | Unpolarized capacitor
C31 | 1 | 4.7uF | C | Capacitor_SMD:C_1206_3216Metric_Pad1.33x1.80mm_HandSolder | Unpolarized capacitor
R29, R32, R33, R39, R40 | 5 | 0R | R_Small | Resistor_SMD:R_0402_1005Metric | Resistor, small symbol
R16, R31, R37, R38 | 4 | 49R9 1% | R_Small | Resistor_SMD:R_0402_1005Metric | Resistor, small symbol
R13 | 1 | 10R 1% | R_Small | Resistor_SMD:R_0402_1005Metric | Resistor, small symbol
R67 | 1 | 10k but unessesary | R | Resistor_SMD:R_0402_1005Metric | Resistor
R12 | 1 | 10k | R_Small | Resistor_SMD:R_0402_1005Metric | Resistor, small symbol
R30 | 1 | 12.4k 1% | R_Small | Resistor_SMD:R_0402_1005Metric | Resistor, small symbol
R27 | 1 | 1M | R_Small | Resistor_SMD:R_0402_1005Metric | Resistor, small symbol
R1, R2 | 2 | 27 | R | Resistor_SMD:R_0402_1005Metric | Resistor
R14, R15 | 2 | 330 | R_Small | Resistor_SMD:R_0402_1005Metric | Resistor, small symbol
R66, R68 | 2 | 1k | R | Resistor_SMD:R_0402_1005Metric | Resistor
R3 | 1 | 5k | R | Resistor_SMD:R_0402_1005Metric | Resistor
R28 | 1 | 0 | R_Small | Resistor_SMD:R_0603_1608Metric | Resistor, small symbol
R5 | 1 | 10k | R_Small | Resistor_SMD:R_0603_1608Metric | Resistor, small symbol
R6 | 1 | 90k | R_Small | Resistor_SMD:R_0603_1608Metric | Resistor, small symbol
R4, R17, R20, R24, R34 | 5 | 680 | R_Small | Resistor_SMD:R_0805_2012Metric_Pad1.20x1.40mm_HandSolder | Resistor, small symbol
R11 | 1 | 100k | R_Small | Resistor_SMD:R_0805_2012Metric_Pad1.20x1.40mm_HandSolder | Resistor, small symbol
R19 | 1 | 1500 | R_Small | Resistor_SMD:R_0805_2012Metric_Pad1.20x1.40mm_HandSolder | Resistor, small symbol
R7, R9 | 2 | 1k | R_Small | Resistor_SMD:R_0805_2012Metric_Pad1.20x1.40mm_HandSolder | Resistor, small symbol
R8, R10 | 2 | 1M | R_Small | Resistor_SMD:R_0805_2012Metric_Pad1.20x1.40mm_HandSolder | Resistor, small symbol
R18, R23 | 2 | 100 | R_Small | Resistor_SMD:R_0805_2012Metric_Pad1.20x1.40mm_HandSolder | Resistor, small symbol
R21, R22 | 2 | 12k | R_Small | Resistor_SMD:R_0805_2012Metric_Pad1.20x1.40mm_HandSolder | Resistor, small symbol
R25, R35 | 2 | 270 | R_Small | Resistor_SMD:R_0805_2012Metric_Pad1.20x1.40mm_HandSolder | Resistor, small symbol
R26, R36 | 2 | 220 | R_Small | Resistor_SMD:R_0805_2012Metric_Pad1.20x1.40mm_HandSolder | Resistor, small symbol
Column1 | Column2 | Column3 | Column4 | Column5 | Column6 | Column7
R_shunt1 | 1 | 1mOhm | PA1206FRE7W0R001Z | SamacSys_Parts:RESC3216X90N | Current Sense Resistors - SMD 1mOhms 1/2W) 50PPM/C 1 % 1206 AEC-Q200
Y2 | 1 | ABM8G-12.000MHZ-4Y-T3 | ABM8G-12.000MHZ-4Y-T3 | ABM8G | Abracon 12MHz Crystal Unit +/-30ppm SMD 4-Pin 3.2 x 2.5 x 1mm
J4 | 1 | Conn_01x02 | Conn_01x02 | Connector_PinHeader_2.54mm:PinHeader_1x02_P2.54mm_Vertical | Generic connector, single row, 01x02, script generated (kicad-library-utils/schlib/autogen/connector/)
JHVA1 | 1 | Conn_01x02 | Conn_01x02 | Connector_PinHeader_2.54mm:PinHeader_1x02_P2.54mm_Vertical | Generic connector, single row, 01x02, script generated (kicad-library-utils/schlib/autogen/connector/)
J5V2 | 1 | Conn_01x03 | Conn_01x03 | Connector_PinHeader_2.54mm:PinHeader_1x03_P2.54mm_Vertical | Generic connector, single row, 01x03, script generated (kicad-library-utils/schlib/autogen/connector/)
JB_or_U1 | 1 | Conn_01x03 | Conn_01x03 | Connector_PinHeader_2.54mm:PinHeader_1x03_P2.54mm_Vertical | Generic connector, single row, 01x03, script generated (kicad-library-utils/schlib/autogen/connector/)
scl0, scl1 | 2 | Conn_01x05 | Conn_01x05 | Connector_PinHeader_2.54mm:PinHeader_1x05_P2.54mm_Vertical | Generic connector, single row, 01x05, script generated (kicad-library-utils/schlib/autogen/connector/)
J5, J6 | 2 | Conn_01x10 | Conn_01x10 | Connector_PinHeader_2.54mm:PinHeader_1x10_P2.54mm_Vertical | Generic connector, single row, 01x10, script generated (kicad-library-utils/schlib/autogen/connector/)
H1, H2, H3, H4 | 4 | MountingHole | MountingHole | MountingHole:MountingHole_3.2mm_M3_DIN965_Pad_TopBottom | Mounting Hole without connection
U2 | 1 | W25Q128JVS | W25Q128JVS | Package_SO:SOIC-8_5.23x5.23mm_P1.27mm | 128Mb Serial Flash Memory, Standard/Dual/Quad SPI, SOIC-8
U1 | 1 | NCP1117-3.3_SOT223 | NCP1117-3.3_SOT223 | Package_TO_SOT_SMD:SOT-223-3_TabPin2 | 1A Low drop-out regulator, Fixed Output 3.3V, SOT-223
J2 | 1 | 2174507-2 | 2174507-2 | SamacSys_Parts:21745072 | Conn Micro USB 2.0 Type B RCP 5 POS 0.65mm Solder RA SMD 5 Terminal 1 Port T/R
S1 | 1 | 4,35E+11 | 4,35E+11 | SamacSys_Parts:435441019830 | Tactile Switches WS-TASV Tact Switch Washable 4.1x2.8x1.9 mm SMT
V_BAT1 | 1 | 502352-0200 | 502352-0200 | SamacSys_Parts:5023520200 | Molex DURACLIK 502352, 2mm Pitch, 2 Way, 1 Row, Right Angle PCB Header, Surface Mount
H1-2 | 1 | 502352-0400 | 502352-0400 | SamacSys_Parts:5023520400 | Molex DURACLIK 502352, 2mm Pitch, 4 Way, 1 Row, Right Angle PCB Header, Surface Mount
H3-8 | 1 | 502352-1210 | 502352-1210 | SamacSys_Parts:5023521210 | DuraClik Wire-to-Board Header, Single Row, Right-Angle, Circuits, Tin (Sn) Plating, Black
Ox0, Ox1, Ox2, Ox3, Ox4, Ox5 | 6 | 560020-0420 | 560020-0420 | SamacSys_Parts:560020-0420 | Molex DURACLIK Series, Series Number 560020, 2mm Pitch 4 Way 1 Row Vertical PCB Header, 3A
L1 | 1 | 74439346068 | 74439346068 | SamacSys_Parts:74439346068 | Wurth WE-XHMI Series Type 6060 Shielded Wire-wound SMD Inductor 6.8 uH +/-20% Wire-Wound 6.5A Idc
FB1 | 1 | BLM18SP102SZ1D | BLM18SP102SZ1D | SamacSys_Parts:BLM18SP221SN1B | Ferrite Beads 0603 1000ohm 25% INFO AEC-Q200
IC5 | 1 | L7805ACD2T-TR | L7805ACD2T-TR | SamacSys_Parts:D2PAK-STB35NF10T4 | Voltage Regulator 5V 1A D2PAK STMicroelectronics L78xx L7805ACD2T-TR, Single Linear Voltage Regulator, 1.5A 5 V, +/-2%, 3-Pin D2PAK
D5, D7, D9 | 3 | D | D | SamacSys_Parts:DIOM5336X245N | Diode
D8 | 1 | RBR2LB60BTBR1 | D | SamacSys_Parts:DIOM5336X245N | Diode
Y1 | 1 | ECS-250-6-33B2-CTP-TR | ECS-250-6-33B2-CTP-TR | SamacSys_Parts:ECS250633B2CTPTR | 25 MHz +/-10ppm Crystal 6pF 40 Ohms 4-SMD, No Lead
J3 | 1 | J1B1211CCD | J1B1211CCD | SamacSys_Parts:J1B1211CCD
V_5V1 | 1 | APTD2012LCGCK | APTD2012LCGCK_1 | SamacSys_Parts:LEDC2012X120N | Standard LEDs - SMD 0805 Dome Lens LED Green- 570nm
V_BATT1 | 1 | APTD2012LCGCK | APTD2012LCGCK_1 | SamacSys_Parts:LEDC2012X120N | Standard LEDs - SMD 0805 Dome Lens LED Green- 570nm
V_LAN1 | 1 | APTD2012LCGCK | APTD2012LCGCK_1 | SamacSys_Parts:LEDC2012X120N | Standard LEDs - SMD 0805 Dome Lens LED Green- 570nm
V_SD1 | 1 | APTD2012LCGCK | APTD2012LCGCK_1 | SamacSys_Parts:LEDC2012X120N | Standard LEDs - SMD 0805 Dome Lens LED Green- 570nm
V_uC1 | 1 | APTD2012LCGCK | APTD2012LCGCK_1 | SamacSys_Parts:LEDC2012X120N | Standard LEDs - SMD 0805 Dome Lens LED Green- 570nm
!V_BAT1 | 1 | APTD2012LSURCK | APTD2012LSURCK_1 | SamacSys_Parts:LEDM2012X120N | Standard LEDs - SMD 0805 Dome Lens LED Red- 630nm
LED1 | 1 | StatusLED | LTRBR37G-4R4S-0125-0 | SamacSys_Parts:LTRBR37G4R4S01250 | Standard LEDs - SMD LTRBR37G
LED_OX1 | 1 | StatusLED | LTRBR37G-4R4S-0125-0 | SamacSys_Parts:LTRBR37G4R4S01250 | Standard LEDs - SMD LTRBR37G
SD1 | 1 | MEM20850011500A | MEM2085-00-115-00-A | SamacSys_Parts:MEM20850011500A | Memory Card Connectors Micro SD Push Pull SMT 1.15mm No Peg
F1 | 1 | MF-LSMF110X-2 | MF-LSMF110X-2 | SamacSys_Parts:MFLSMF110X2 | 2920 Resettable SMD PPTC 1.1A/33V
J1 | 1 | SC0914_7_ | SC0914_7_ | SamacSys_Parts:QFN40P700X700X90-57N-D
IC4 | 1 | LM324QT | LM324QT | SamacSys_Parts:QFN50P300X300X100-17N | Operational Amplifiers - Op Amps Low Power QUAD 1.3 MHz 100dB
IC2 | 1 | W5500 | W5500 | SamacSys_Parts:QFP50P900X900X160-48N | Ethernet ICs 3in1 Enet Controller TCP/IP +MAC+PHY
IC1 | 1 | MAX3485AEASA+T | MAX3485AEASA+T | SamacSys_Parts:SOIC127P600X175-8N | MAXIM INTEGRATED PRODUCTS - MAX3485AEASA+T - RS422 / RS485 Transceiver, 1 Driver, 1 Receiver, 3V to 3.6V Supply, NSOIC-8
MUXH1 | 1 | PCA9555PW,112 | PCA9555PW,112_1 | SamacSys_Parts:SOP65P640X110-24N | PCA9555 16-bit I2C-bus and SMBus I/O port with interrupt
V_shifter1 | 1 | TXS0108EQPWRQ1 | TXS0108EQPWRQ1 | SamacSys_Parts:SOP65P640X120-20N | 8-Bit Bi-directional, Level-Shifting, Voltage Translator for Open-Drain and Push-Pull Applications
ICH0, ICH1, ICH2, ICH3, ICH4, ICH5, ICH6, ICH7 | 8 | ITS4200S-ME-O | ITS4200S-ME-O | SamacSys_Parts:SOT230P700X170-4N | Power Switch ICs - Power Distribution MINI-PROFET
3VLIN1, 3VLIN2 | 2 | LM3940IMP-3.3_NOPB | LM3940IMP-3.3_NOPB | SamacSys_Parts:SOT230P700X180-4N | LM3940IMP-3.3/NOPB, Low Dropout Voltage Regulator, 1A, 3.3 V, 4.5 7.5 Vin, 4-Pin SOT-223
BUCK1 | 1 | TPS62933DRLR | TPS62933DRLR | SamacSys_Parts:SOTFL50P160X60-8N | The TPS62933 is a high-efficiency, easy-to-use synchronous buck converter with a wide input voltage range of 3.8 V to 30 V

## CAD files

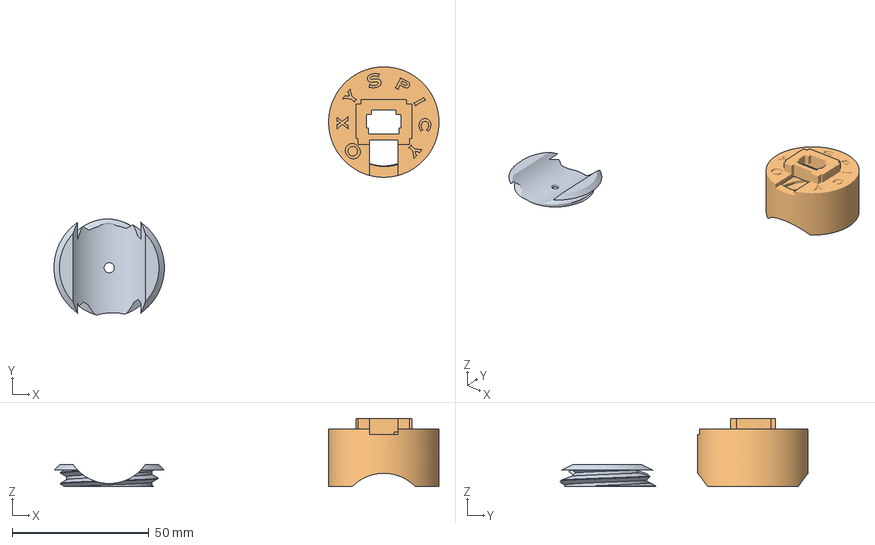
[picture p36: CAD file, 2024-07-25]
motherboard/Hardware/FD_OEM Case/FD-OEM Case.3mf
140.5 x 90.6 x 25.0 mm
FD-OEM Cover V2 v4.stl_1
FD-OEM Case Body (1).stl

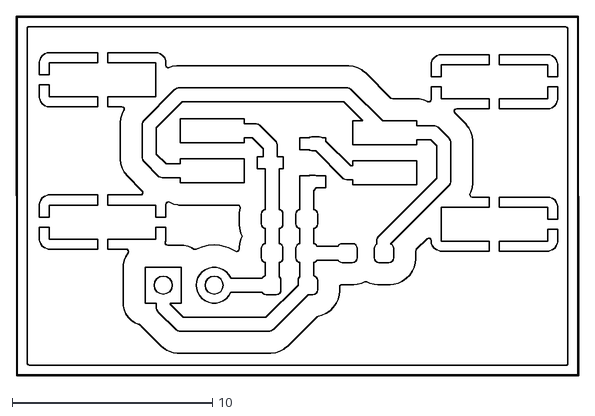
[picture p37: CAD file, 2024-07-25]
motherboard/Hardware/Inrush_current_limiter/Inrush_current_limiter-F_Cu.dxf
28.0 x 18.0

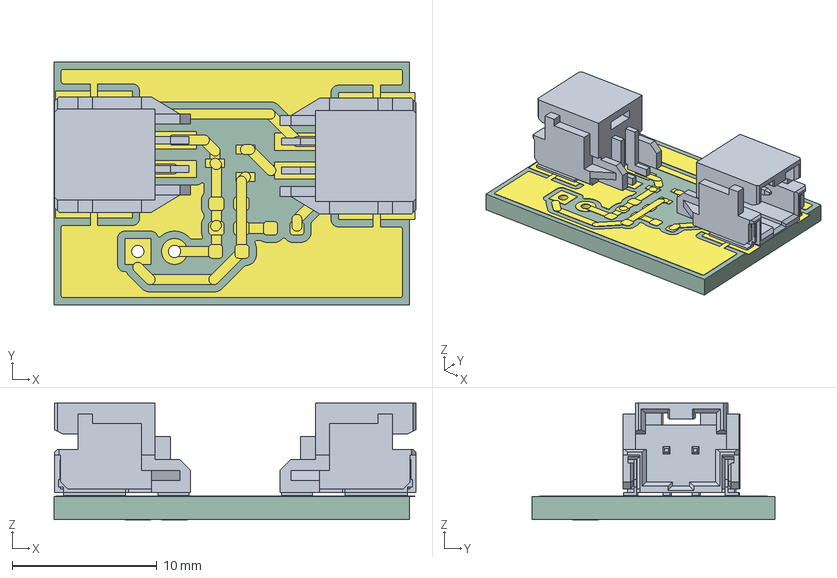
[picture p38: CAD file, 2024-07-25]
motherboard/Hardware/Inrush_current_limiter/Inrush_current_limiter.step
25.1 x 16.8 x 8.09 mm
_autosave-Inrush_current_limiter_track_1
_autosave-Inrush_current_limiter_track_2
_autosave-Inrush_current_limiter_track_3
_autosave-Inrush_current_limiter_track_4
_autosave-Inrush_current_limiter_track_5
_autosave-Inrush_current_limiter_track_6
_autosave-Inrush_current_limiter_track_7
_autosave-Inrush_current_limiter_track_8
_autosave-Inrush_current_limiter_track_9
_autosave-Inrush_current_limiter_track_10
_autosave-Inrush_current_limiter_track_11
_autosave-Inrush_current_limiter_track_12
_autosave-Inrush_current_limiter_track_13
_autosave-Inrush_current_limiter_track_14
_autosave-Inrush_current_limiter_track_15
_autosave-Inrush_current_limiter_track_16
_autosave-Inrush_current_limiter_track_17
_autosave-Inrush_current_limiter_track_18
_autosave-Inrush_current_limiter_track_19
_autosave-Inrush_current_limiter_track_20
_autosave-Inrush_current_limiter_track_21
_autosave-Inrush_current_limiter_track_22
_autosave-Inrush_current_limiter_track_23
_autosave-Inrush_current_limiter_track_24
_autosave-Inrush_current_limiter_track_25
_autosave-Inrush_current_limiter_track_26
_autosave-Inrush_current_limiter_track_27
_autosave-Inrush_current_limiter_track_28
_autosave-Inrush_current_limiter_track_29
_autosave-Inrush_current_limiter_track_30
_autosave-Inrush_current_limiter_track_31
_autosave-Inrush_current_limiter_zone
_autosave-Inrush_current_limiter_pad_1
_autosave-Inrush_current_limiter_pad_2
_autosave-Inrush_current_limiter_pad_3
_autosave-Inrush_current_limiter_pad_4
_autosave-Inrush_current_limiter_pad_5
_autosave-Inrush_current_limiter_pad_6
_autosave-Inrush_current_limiter_pad_7
_autosave-Inrush_current_limiter_pad_8
_autosave-Inrush_current_limiter_pad_9
_autosave-Inrush_current_limiter_pad_10
_autosave-Inrush_current_limiter_pad_11
_autosave-Inrush_current_limiter_pad_12
_autosave-Inrush_current_limiter_pad_13
_autosave-Inrush_current_limiter_pad_14
_autosave-Inrush_current_limiter_pad_15
_autosave-Inrush_current_limiter_pad_16
_autosave-Inrush_current_limiter_pad_17
_autosave-Inrush_current_limiter_pad_18
_autosave-Inrush_current_limiter_pad_19
_autosave-Inrush_current_limiter_pad_20
_autosave-Inrush_current_limiter_pad_21
_autosave-Inrush_current_limiter_pad_22
_autosave-Inrush_current_limiter_pad_23
_autosave-Inrush_current_limiter_pad_24
_autosave-Inrush_current_limiter_pad_25
_autosave-Inrush_current_limiter_PCB

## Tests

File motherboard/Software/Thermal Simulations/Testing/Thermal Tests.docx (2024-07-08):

Thermal Tests

Description | Setup | Plot

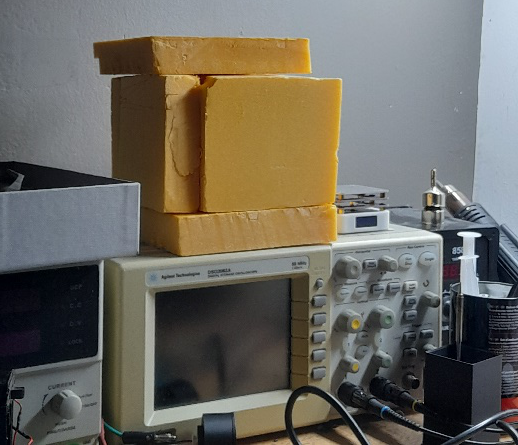
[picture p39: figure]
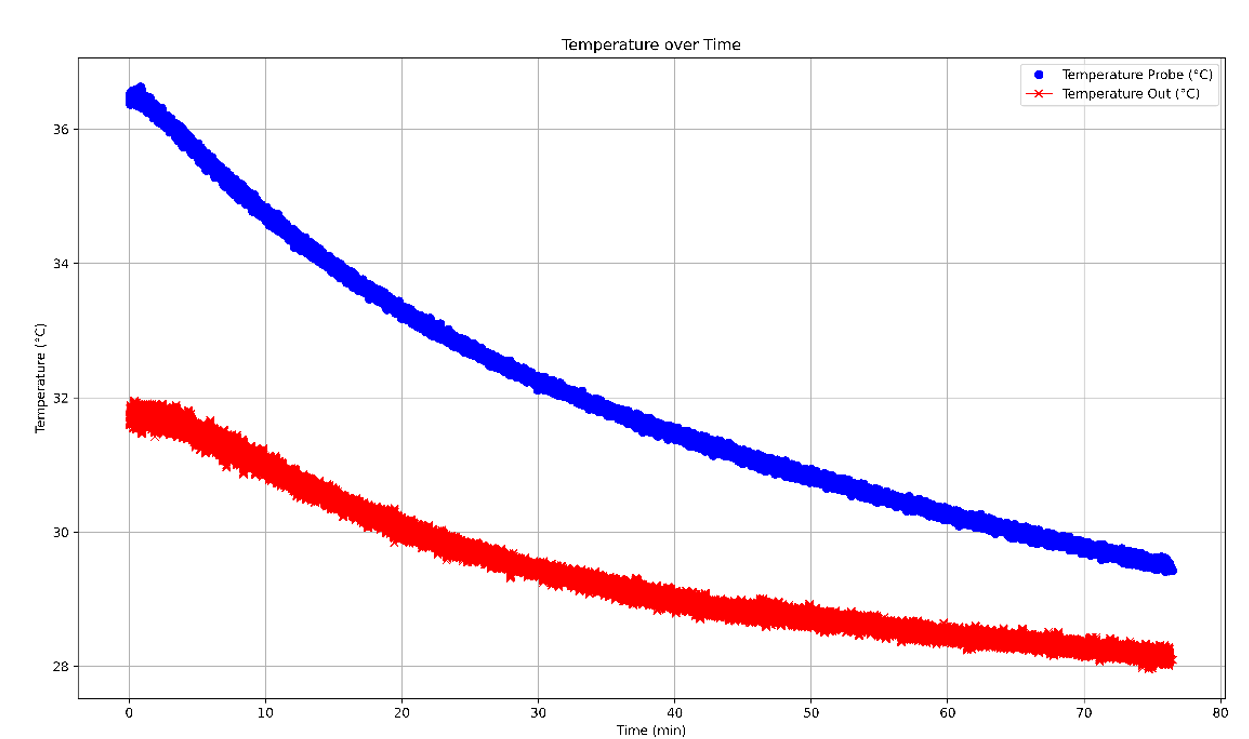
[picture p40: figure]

Cooling down in an isolating Box Temp Out is temperature outside of the tube but still inside the box Room temp

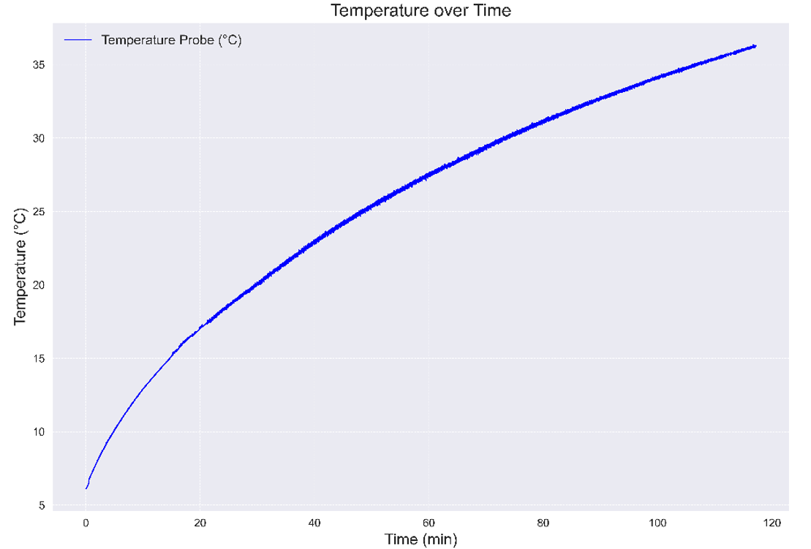
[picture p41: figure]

2,5W Einheitssprungantwort (step response function in an isolating Box) Room temp

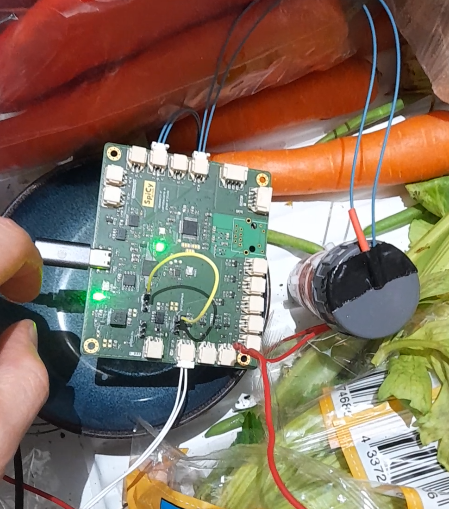
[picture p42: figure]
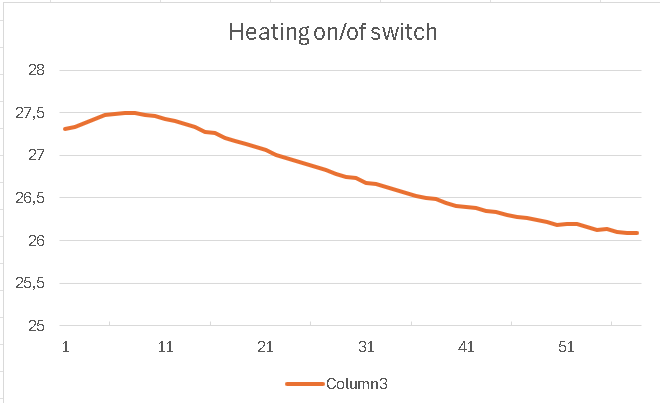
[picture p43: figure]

2.5W On/OF based heating tested without isolation in a fridge - Not enough power to keep up

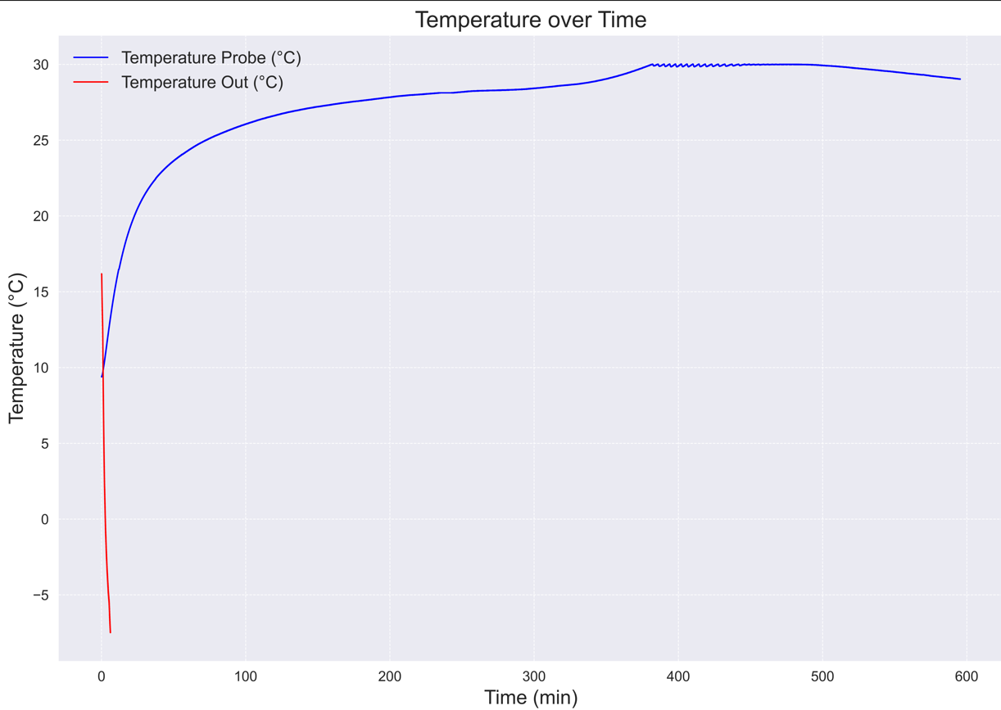
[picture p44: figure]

2.5W On/OF based heating tested with isolation in a freezer Freezer temp around 5°C

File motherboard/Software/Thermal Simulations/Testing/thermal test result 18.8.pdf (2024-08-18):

31

SpiCy BEXUS

thermal tests | Cube | Room Temperature

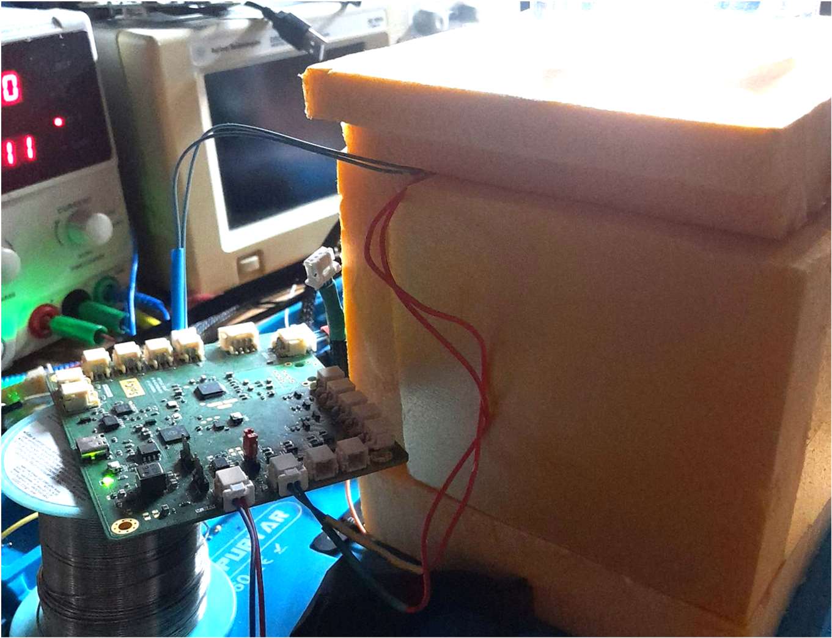
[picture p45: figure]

SOFTWARE | EMBEDDED SOFTWARE

32

SpiCy BEXUS

thermal tests | Cube | SetTemp=34 | kp=4 ki=0.008 ki_max=0.4

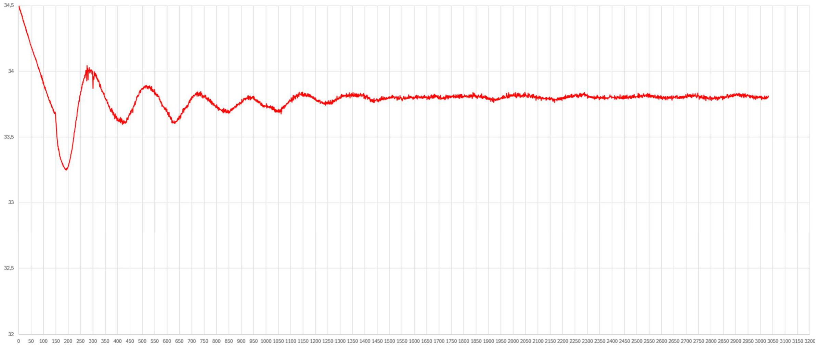
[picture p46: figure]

SOFTWARE | EMBEDDED SOFTWARE

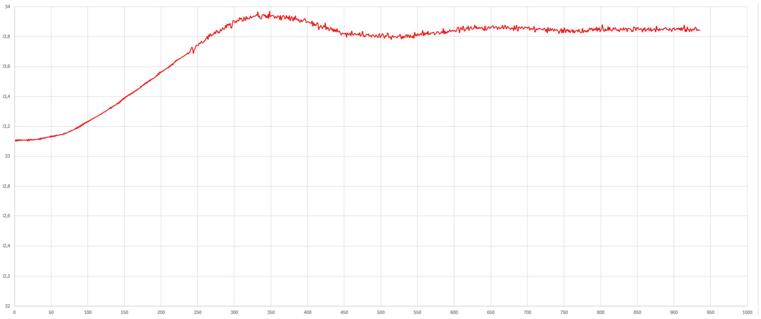
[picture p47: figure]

33

SpiCy BEXUS

thermal tests | Cube | SetTemp=34 | kp=8 ki=0.0004 ki_max=0.1
SOFTWARE | EMBEDDED SOFTWARE

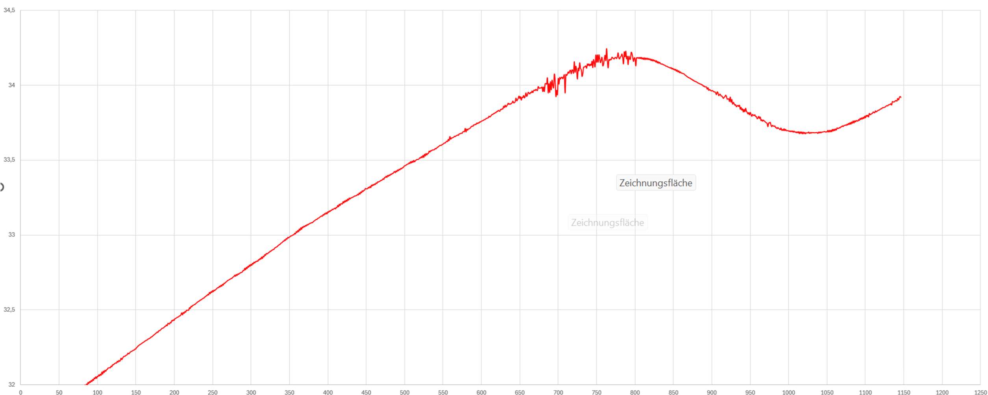
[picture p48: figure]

34

SpiCy BEXUS

thermal tests | Cube | SetTemp=34 | kp=4 ki=0.1 ki_max=3
SOFTWARE | EMBEDDED SOFTWARE


35

SpiCy BEXUS

thermal tests | Cube | Step Response Function | 2.5W
SOFTWARE | EMBEDDED SOFTWARE

## blue = recorded temp red = linear approximation

31

SpiCy BEXUS

Thermal Tests | Module | Variation in Temperatur in Fynn‘s Fridge


SOFTWARE | EMBEDDED SOFTWARE


32

SpiCy BEXUS

Thermal Tests | Module | 2.5W Step Response | Fynn‘s Fridge | [first recoding]
SOFTWARE | EMBEDDED SOFTWARE


32

SpiCy BEXUS

Thermal Tests | Module | 2.5W Step Response | Fynn‘s Fridge | [second recording]
SOFTWARE | EMBEDDED SOFTWARE blue = step response [first]
orage = step response [second]

32

SpiCy BEXUS

Thermal Tests | Module | 2.5W Step Response | Fynn‘s Fridge | [first recording]


SOFTWARE | EMBEDDED SOFTWARE

blue = step response
lila = temp uC
orage = temp Motherboard

SpiCy BEXUS

Thermal Tests | Module | 2.5W Step Response | Fynn‘s Fridge | [first recording]

blue = step response
orage = linear aproximation

SOFTWARE | EMBEDDED SOFTWARE

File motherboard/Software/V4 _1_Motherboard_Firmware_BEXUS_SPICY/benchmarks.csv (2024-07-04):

benchmark | description | time
single_packet_transfer | sends one packet via tcp | 300us i think?
single_oxy_readout | reads oxygen from one probe | 1s

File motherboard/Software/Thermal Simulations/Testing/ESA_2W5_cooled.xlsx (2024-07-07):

timestamp[ms] | temp_probe[°C] | temp_out[°C] | Column1 | Column2 | Column3
68582 | 2731 | 1961 |  | 1.143033333 | 27.31
128583 | 2733 | 1713 |  | 2.14305 | 27.33
188584 | 2738 | 1553 |  | 3.143066667 | 27.38
248585 | 2743 | 1443 |  | 4.143083333 | 27.43
308586 | 2748 | 1371 |  | 5.1431 | 27.48
368587 | 2749 | 1318 |  | 6.143116667 | 27.49
428588 | 2750 | 1288 |  | 7.143133333 | 27.5
488589 | 2750 | 1262 |  | 8.14315 | 27.5
548590 | 2747 | 1232 |  | 9.143166667 | 27.47
608591 | 2746 | 1223 |  | 10.14318333 | 27.46
668592 | 2743 | 1206 |  | 11.1432 | 27.43
728593 | 2740 | 1195 |  | 12.14321667 | 27.4
788594 | 2737 | 1185 |  | 13.14323333 | 27.37
848595 | 2733 | 1176 |  | 14.14325 | 27.33
908596 | 2727 | 1161 |  | 15.14326667 | 27.27
968597 | 2726 | 1161 |  | 16.14328333 | 27.26
1028598 | 2721 | 1149 |  | 17.1433 | 27.21
1088599 | 2717 | 1142 |  | 18.14331667 | 27.17
1148600 | 2713 | 1133 |  | 19.14333333 | 27.13
1208601 | 2710 | 1140 |  | 20.14335 | 27.1
1268602 | 2706 | 1134 |  | 21.14336667 | 27.06
1328603 | 2701 | 1116 |  | 22.14338333 | 27.01
1388604 | 2697 | 1112 |  | 23.1434 | 26.97
1448605 | 2693 | 1107 |  | 24.14341667 | 26.93
1508606 | 2690 | 1106 |  | 25.14343333 | 26.9
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

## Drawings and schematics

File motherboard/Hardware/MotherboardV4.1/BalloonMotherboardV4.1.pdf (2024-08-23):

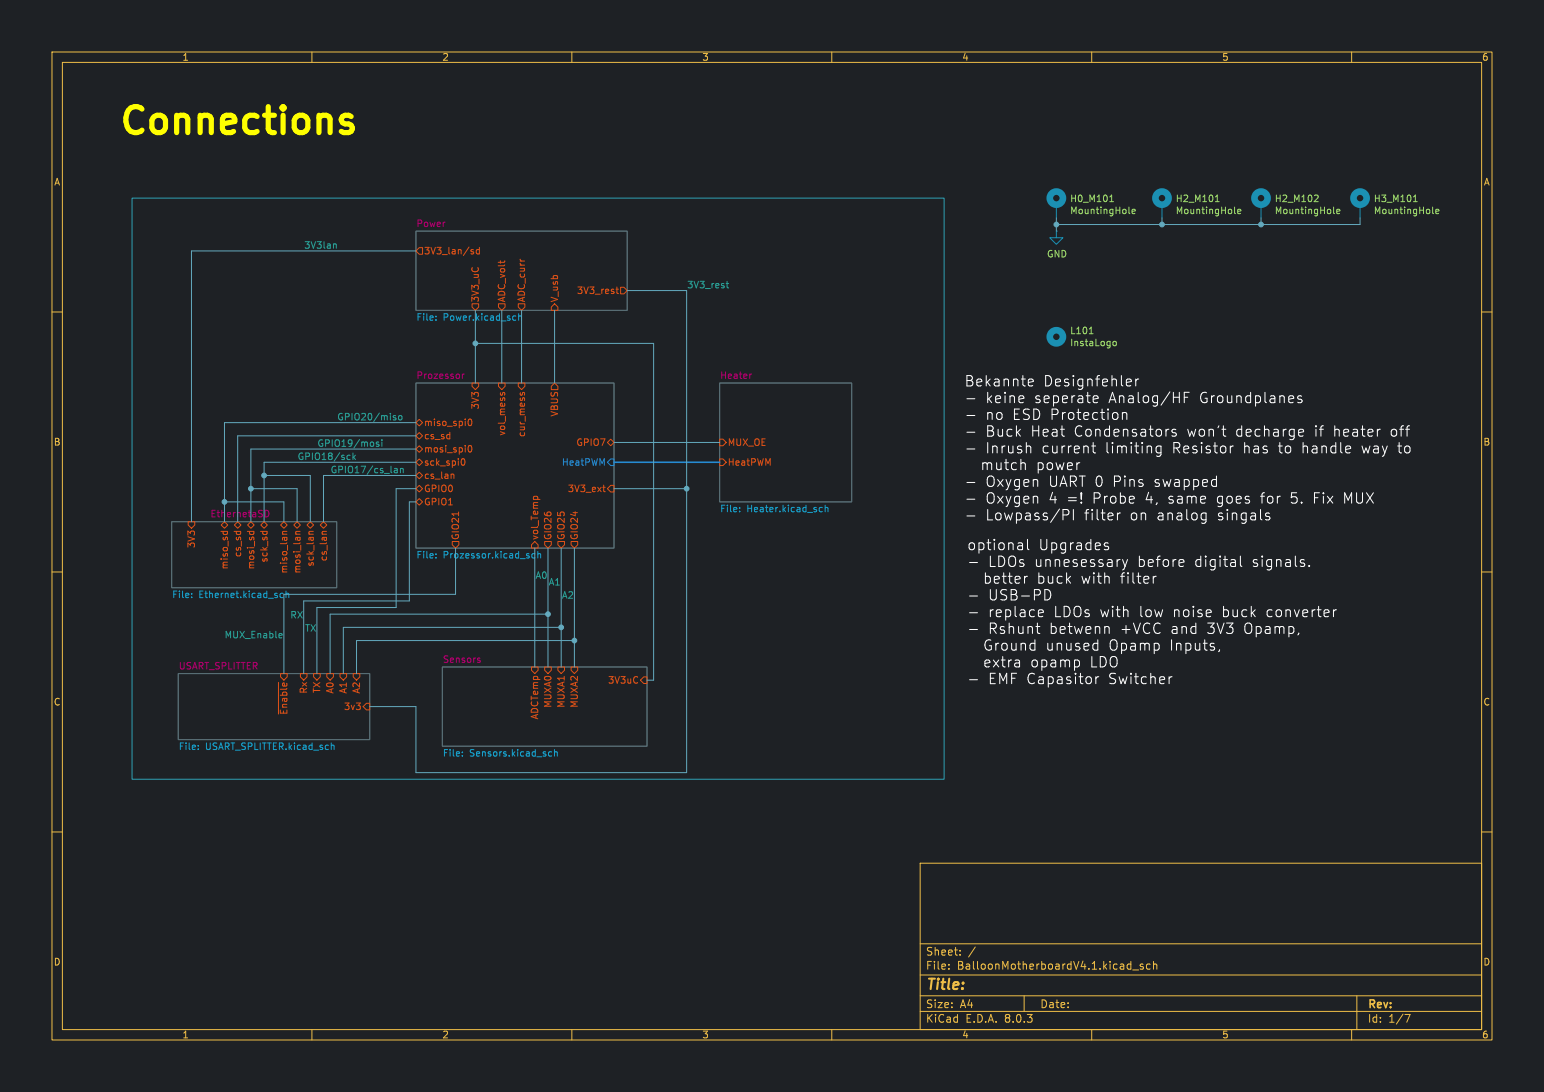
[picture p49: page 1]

mutch power
- Oxygen UART 0 Pins swapped
- Oxygen 4 =! Probe 4, same goes for 5. Fix MUX
better buck with filter
- USB-PD
- replace LDOs with low noise buck converter
- Rshunt betwenn +VCC and 3V3 Opamp,
Ground unused Opamp Inputs,
extra opamp LDO
- EMF Capasitor Switcher

Id: 1/7 Title: File: BalloonMotherboardV4.1.kicad_sch Sheet: /

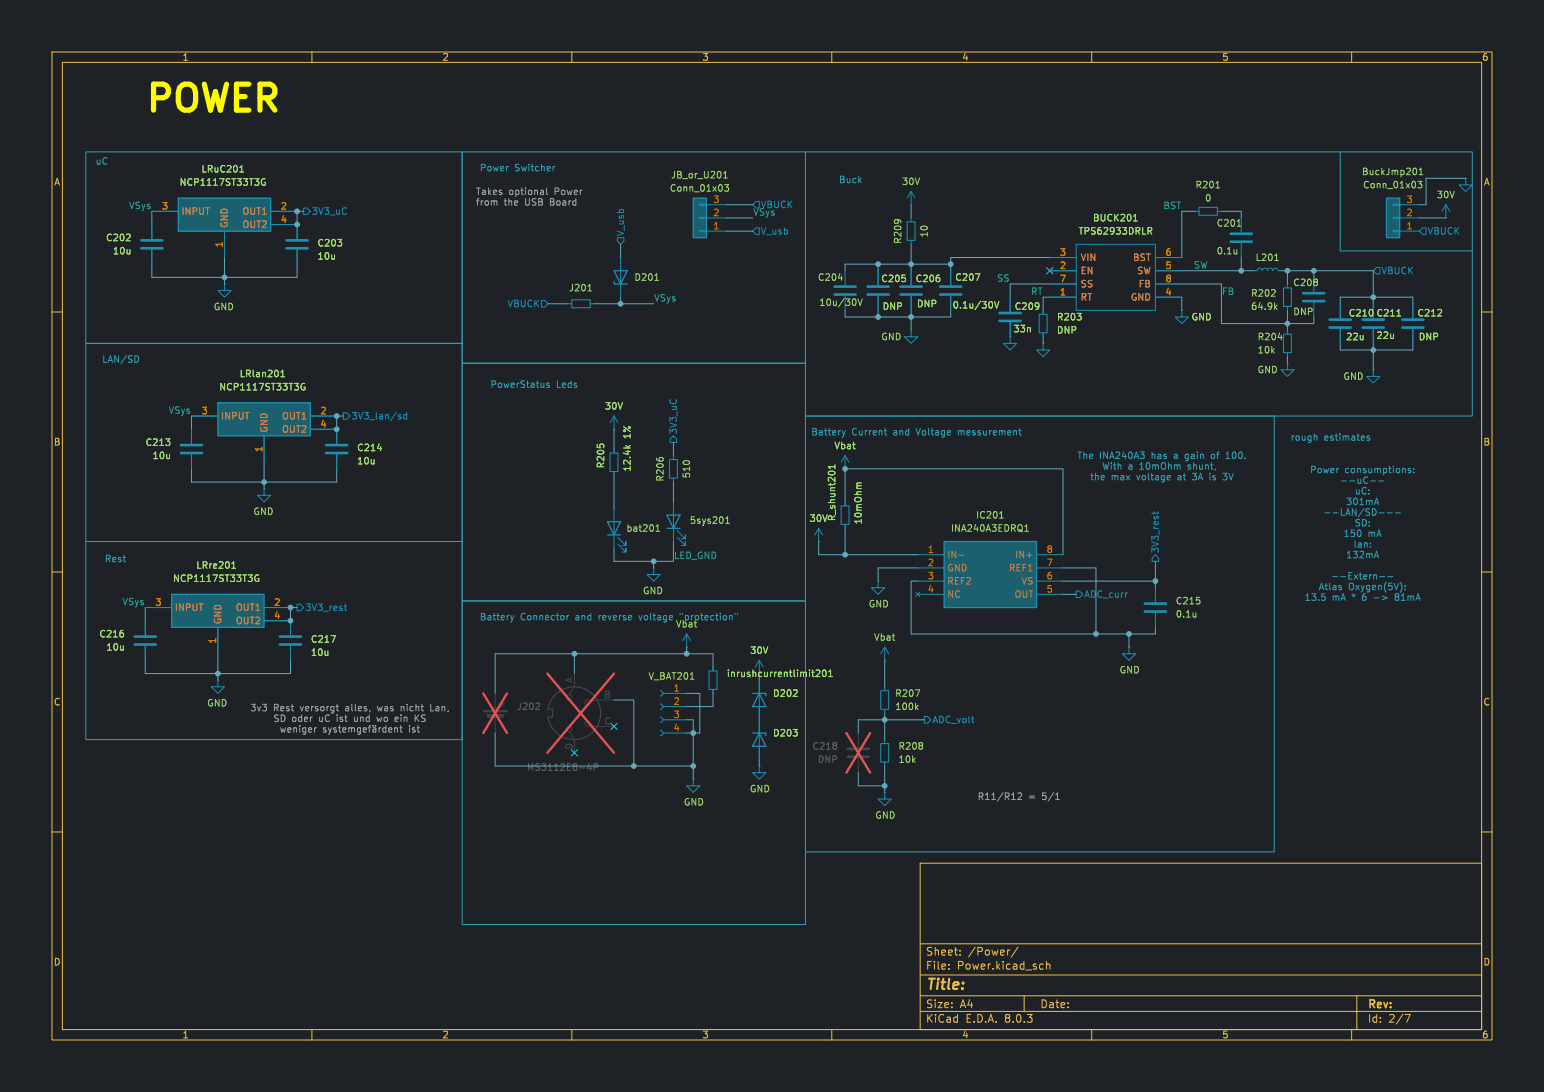
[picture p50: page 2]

The INA240A3 has a gain of 100. With a 10mOhm shunt,

--LAN/SD--- SD: 150 mA

Id: 2/7 Title: File: Power.kicad_sch Sheet: /Power/ GND

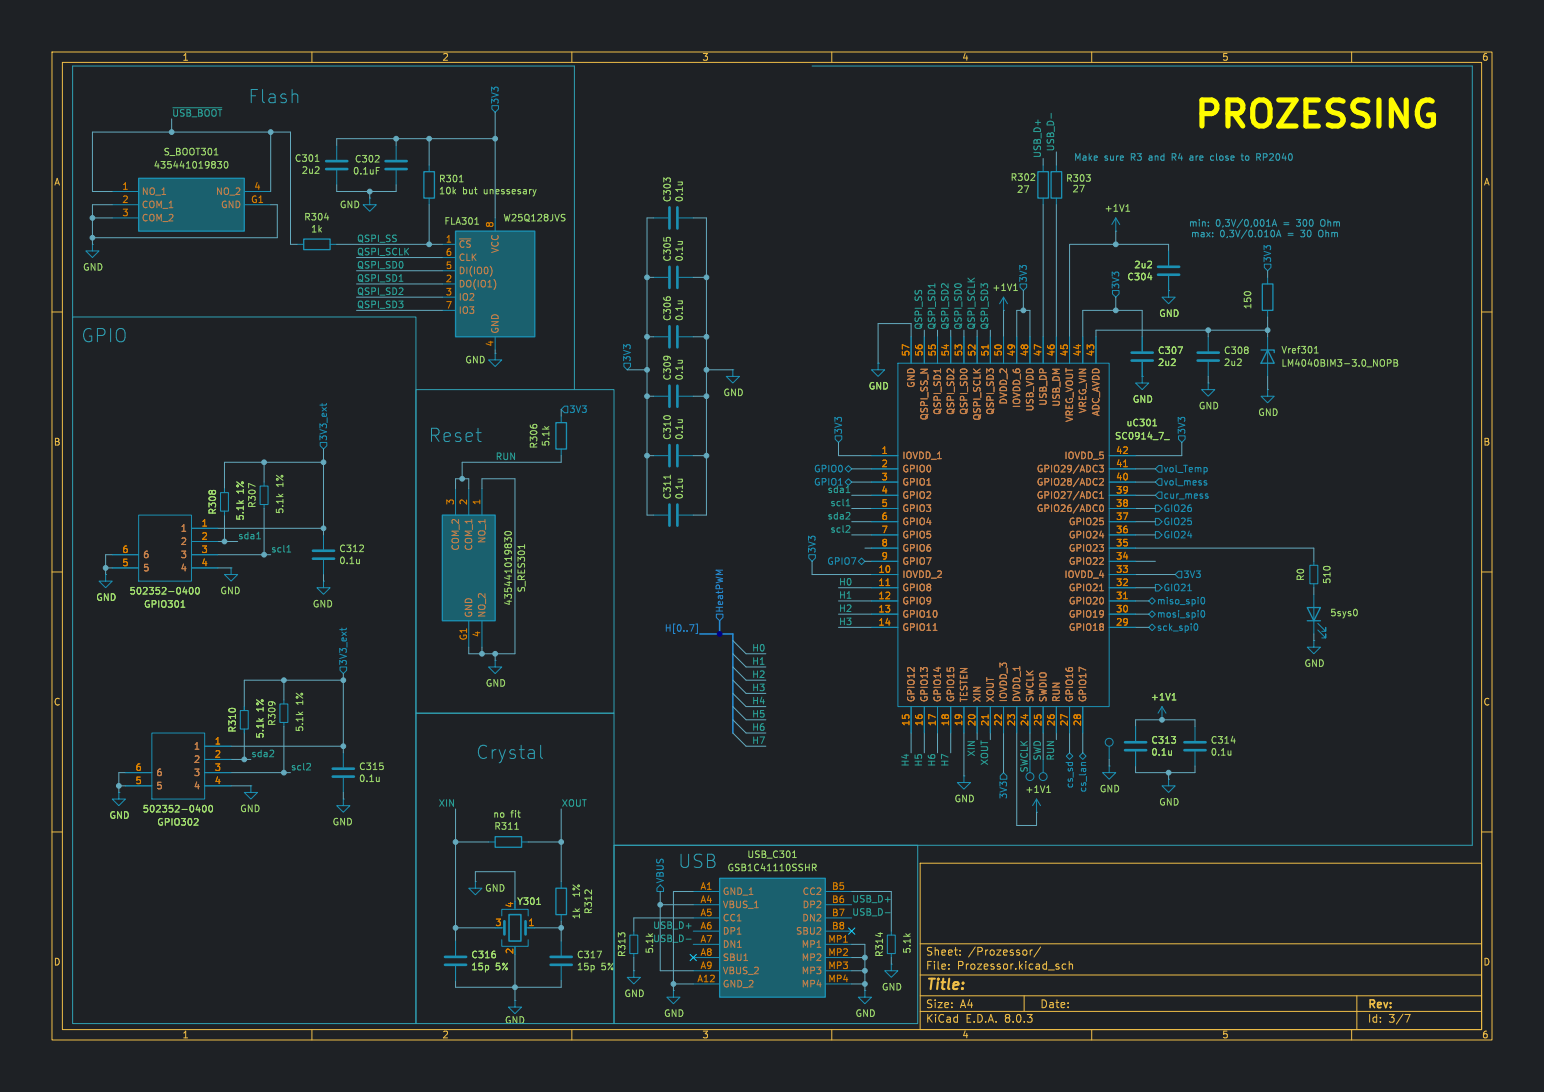
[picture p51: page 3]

Make sure R3 and R4 are close to RP2040 GPIO

Id: 3/7 Title: File: Prozessor.kicad_sch Sheet: /Prozessor/ GND

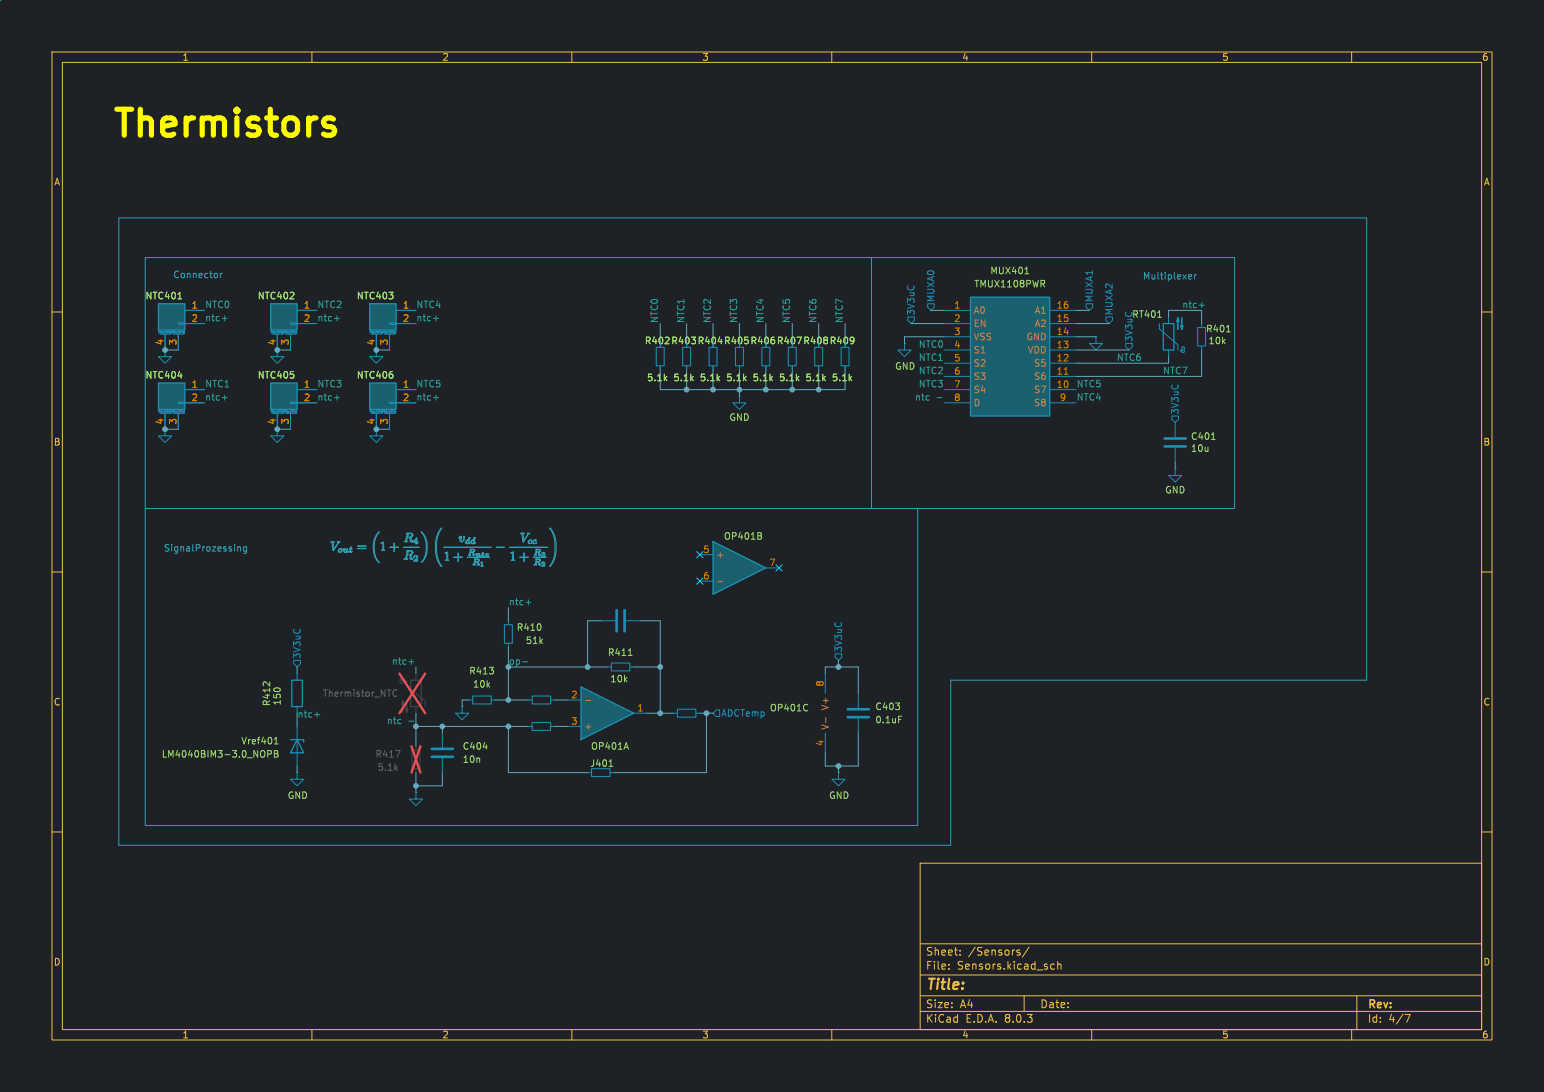
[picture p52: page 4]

Id: 4/7 Title: File: Sensors.kicad_sch Sheet: /Sensors/

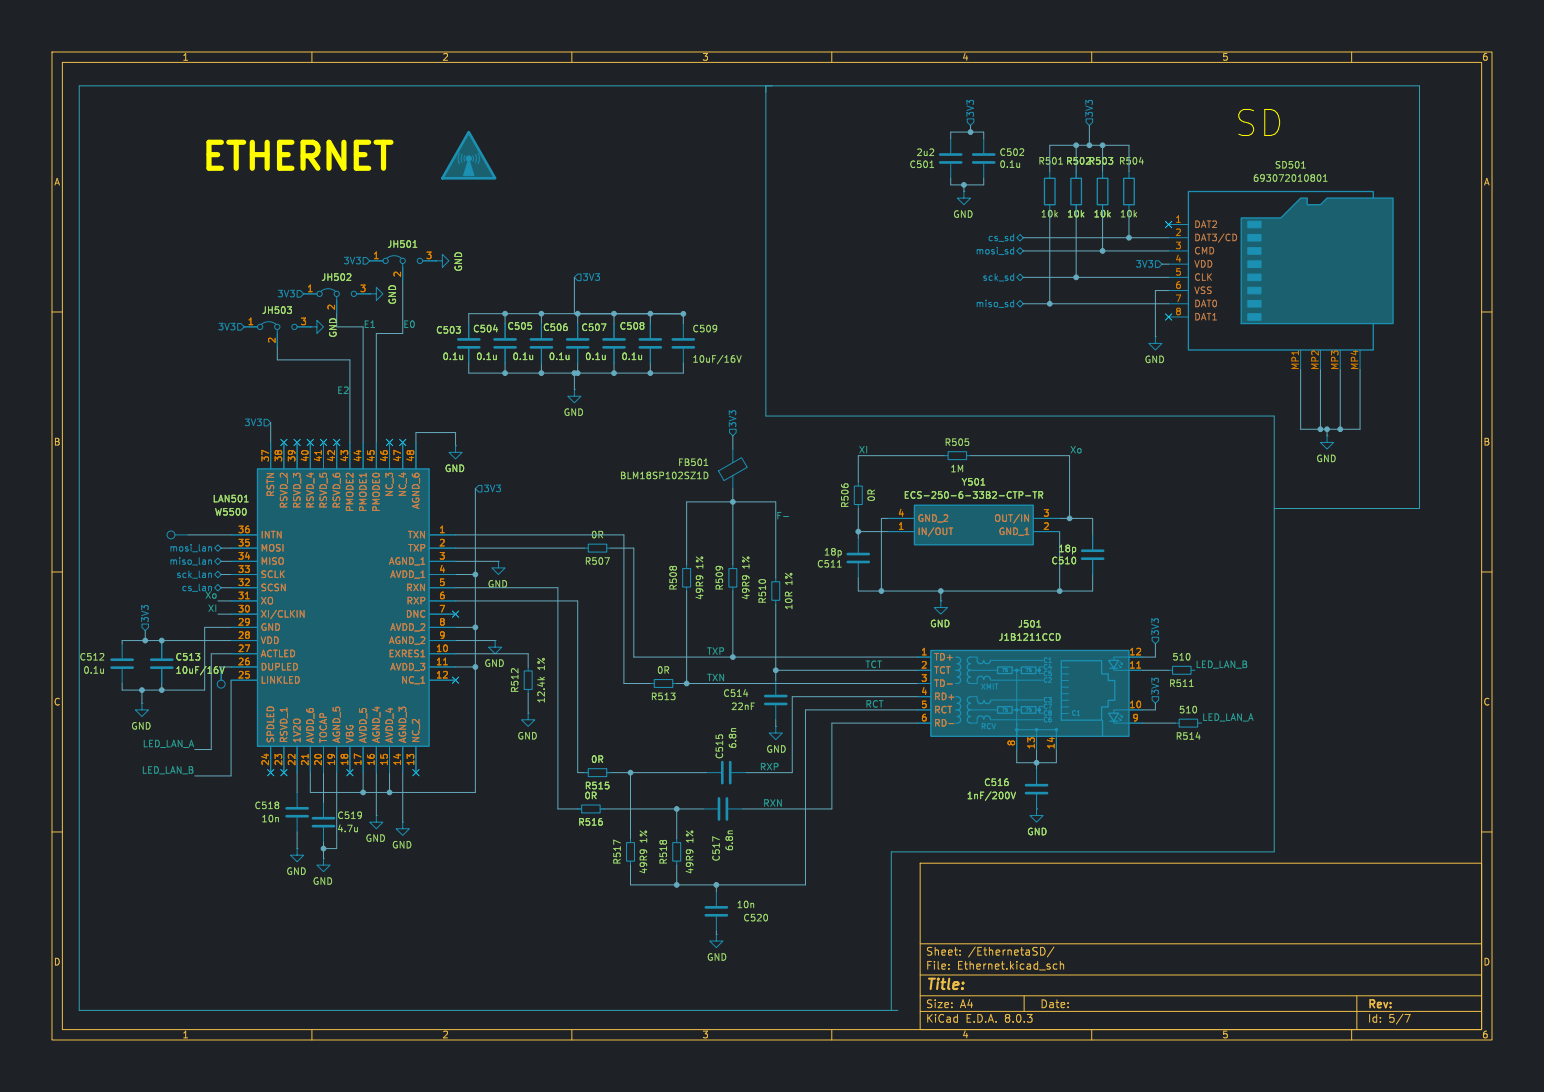
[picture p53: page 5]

Id: 5/7 Title: File: Ethernet.kicad_sch Sheet: /EthernetaSD/ GND

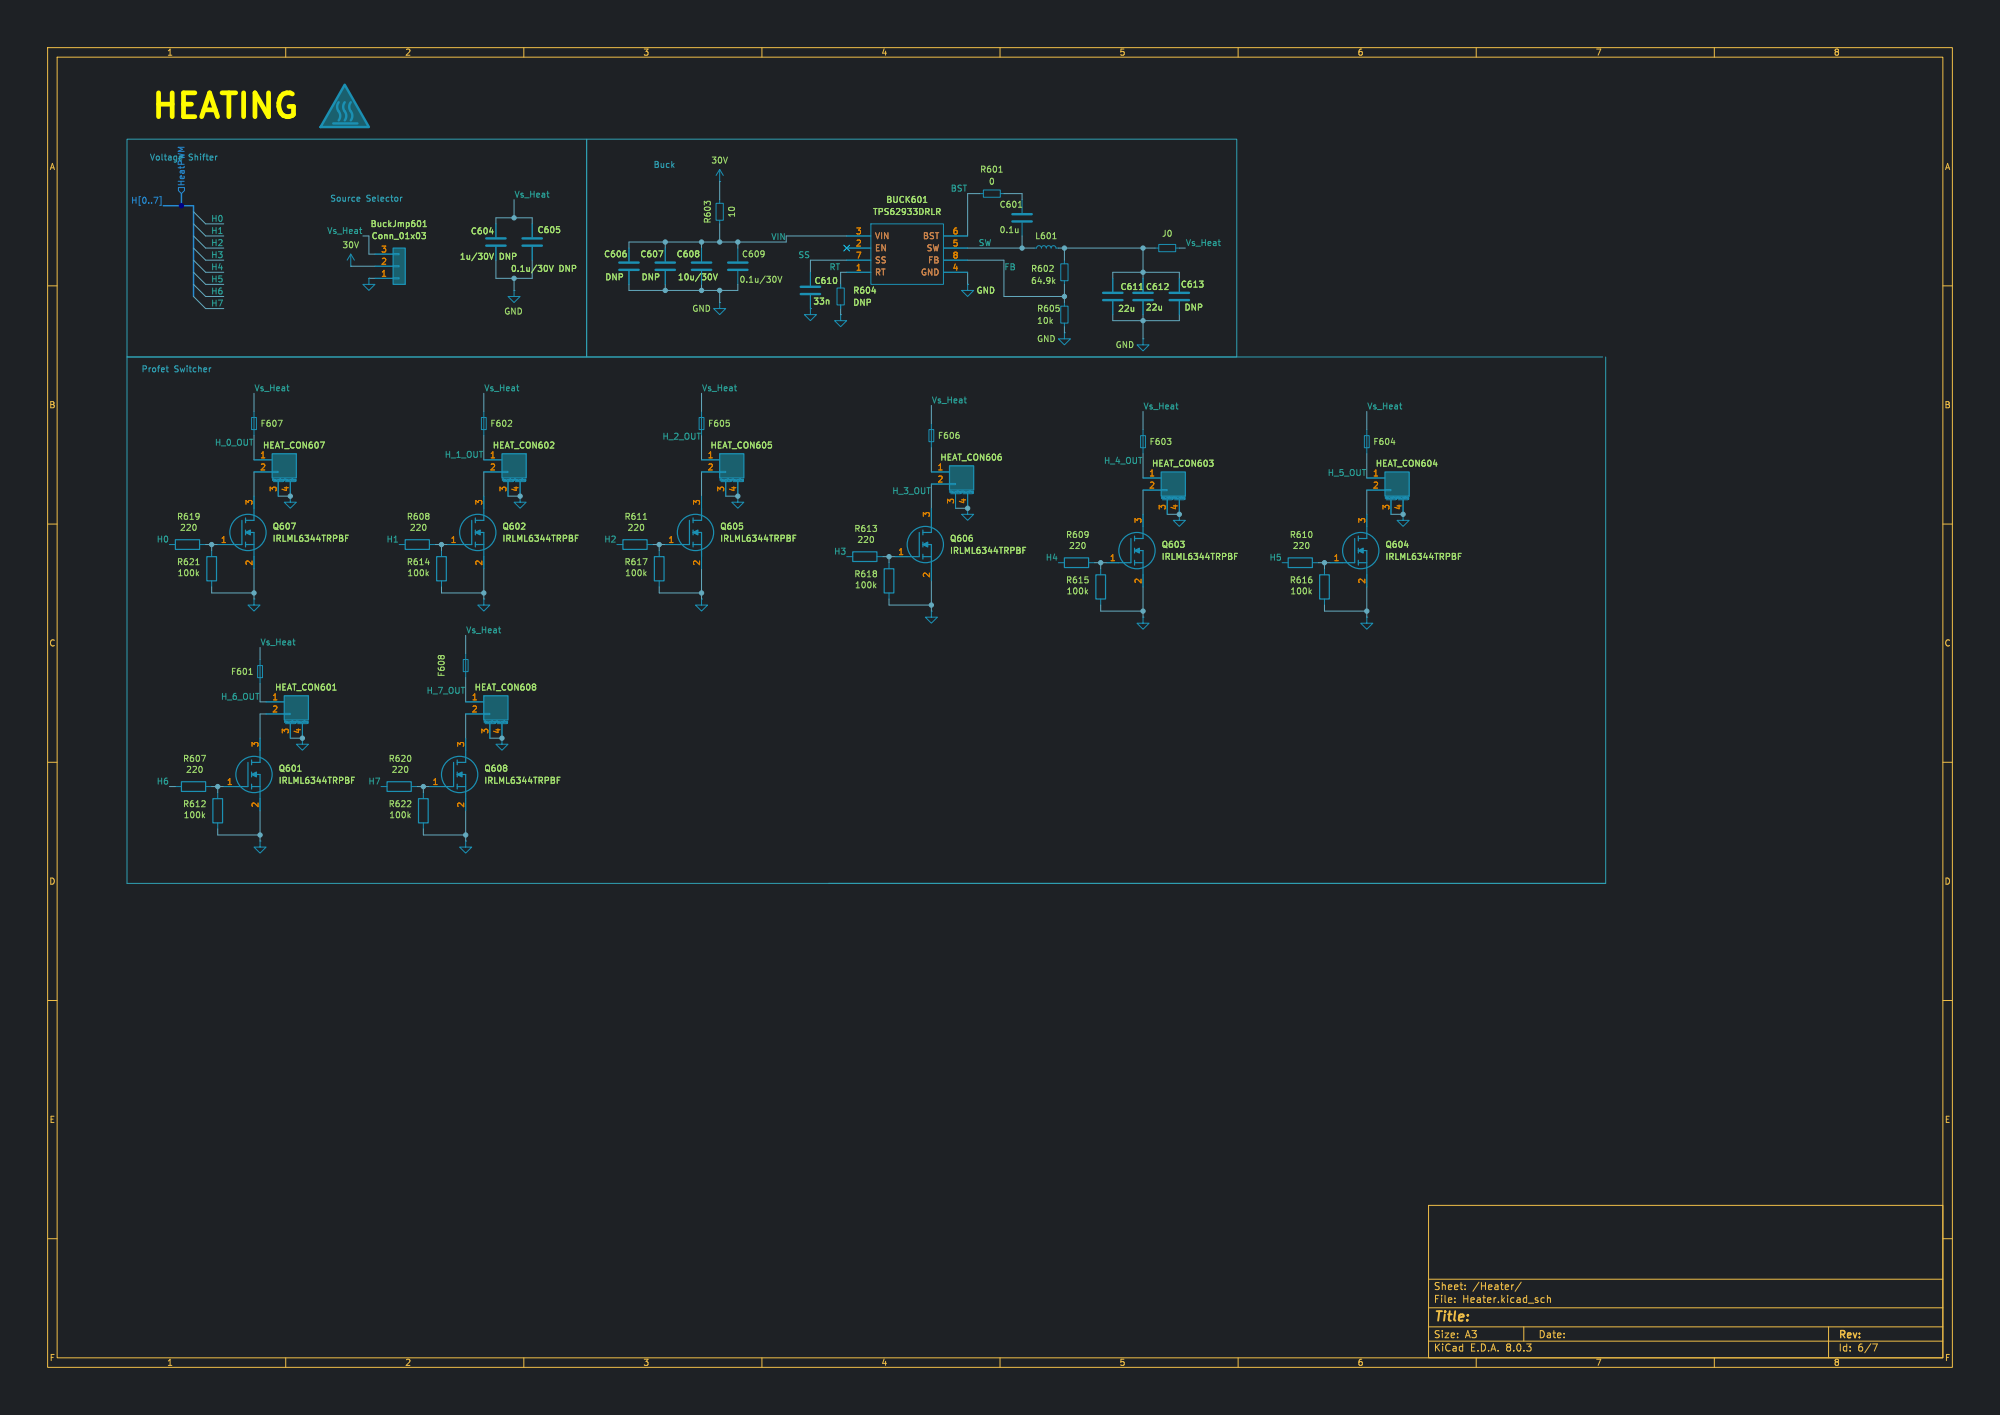
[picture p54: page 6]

Buck Source Selector Profet Switcher Voltage Shifter HEATING

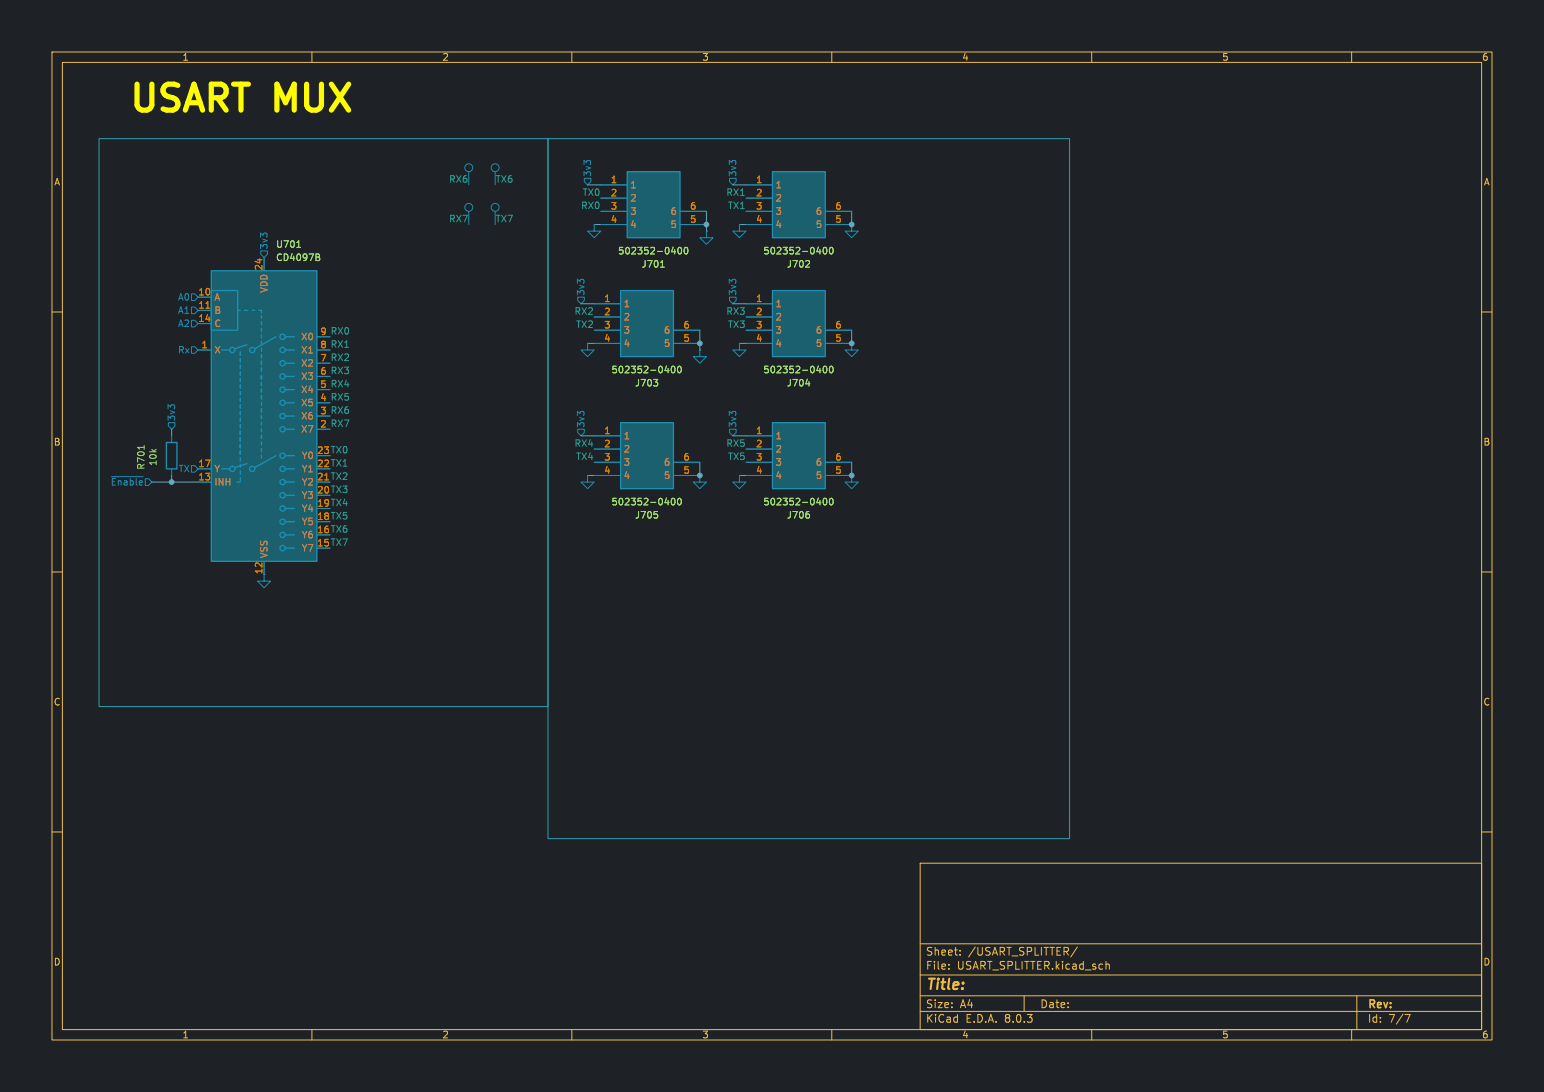
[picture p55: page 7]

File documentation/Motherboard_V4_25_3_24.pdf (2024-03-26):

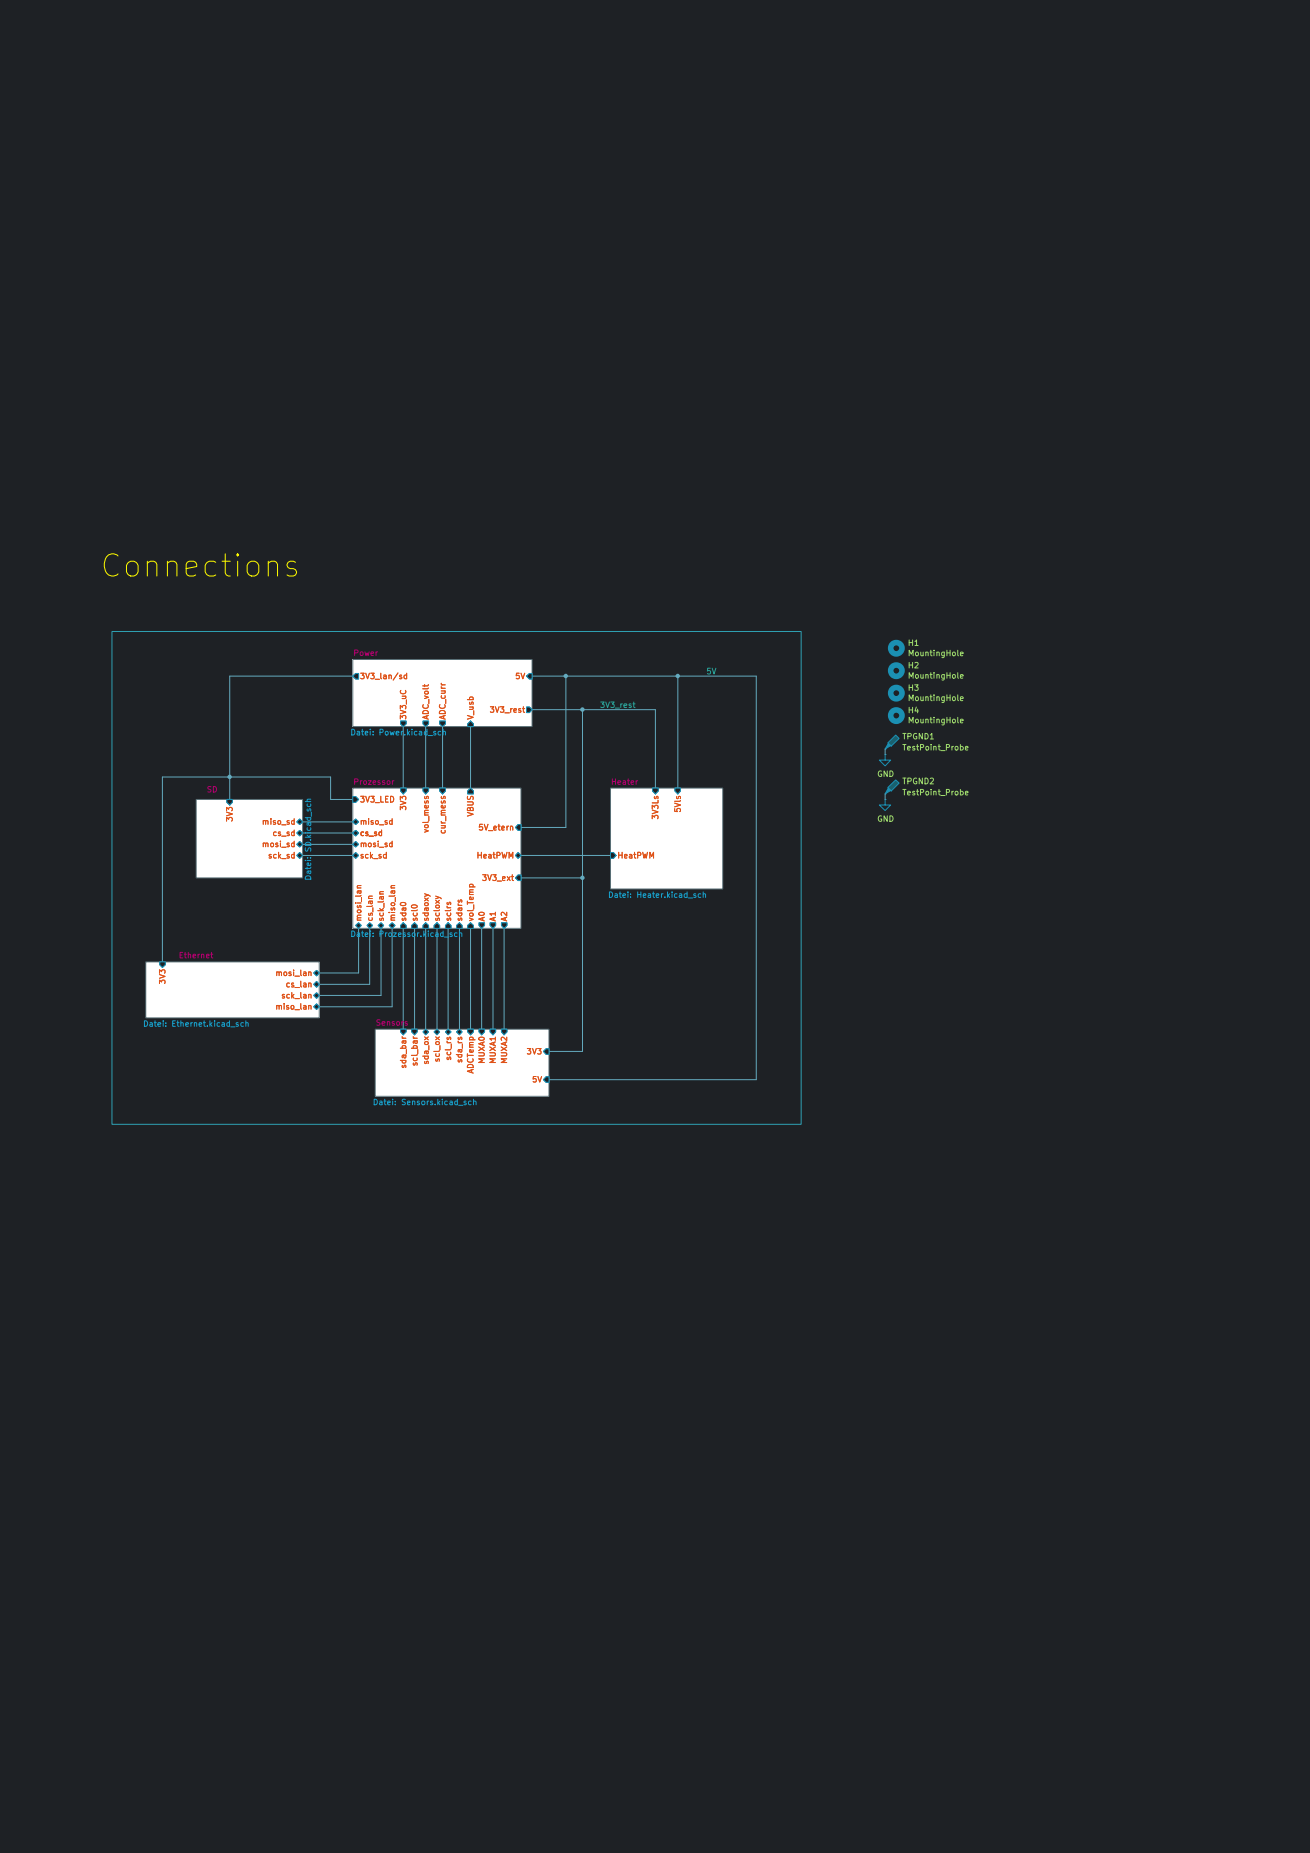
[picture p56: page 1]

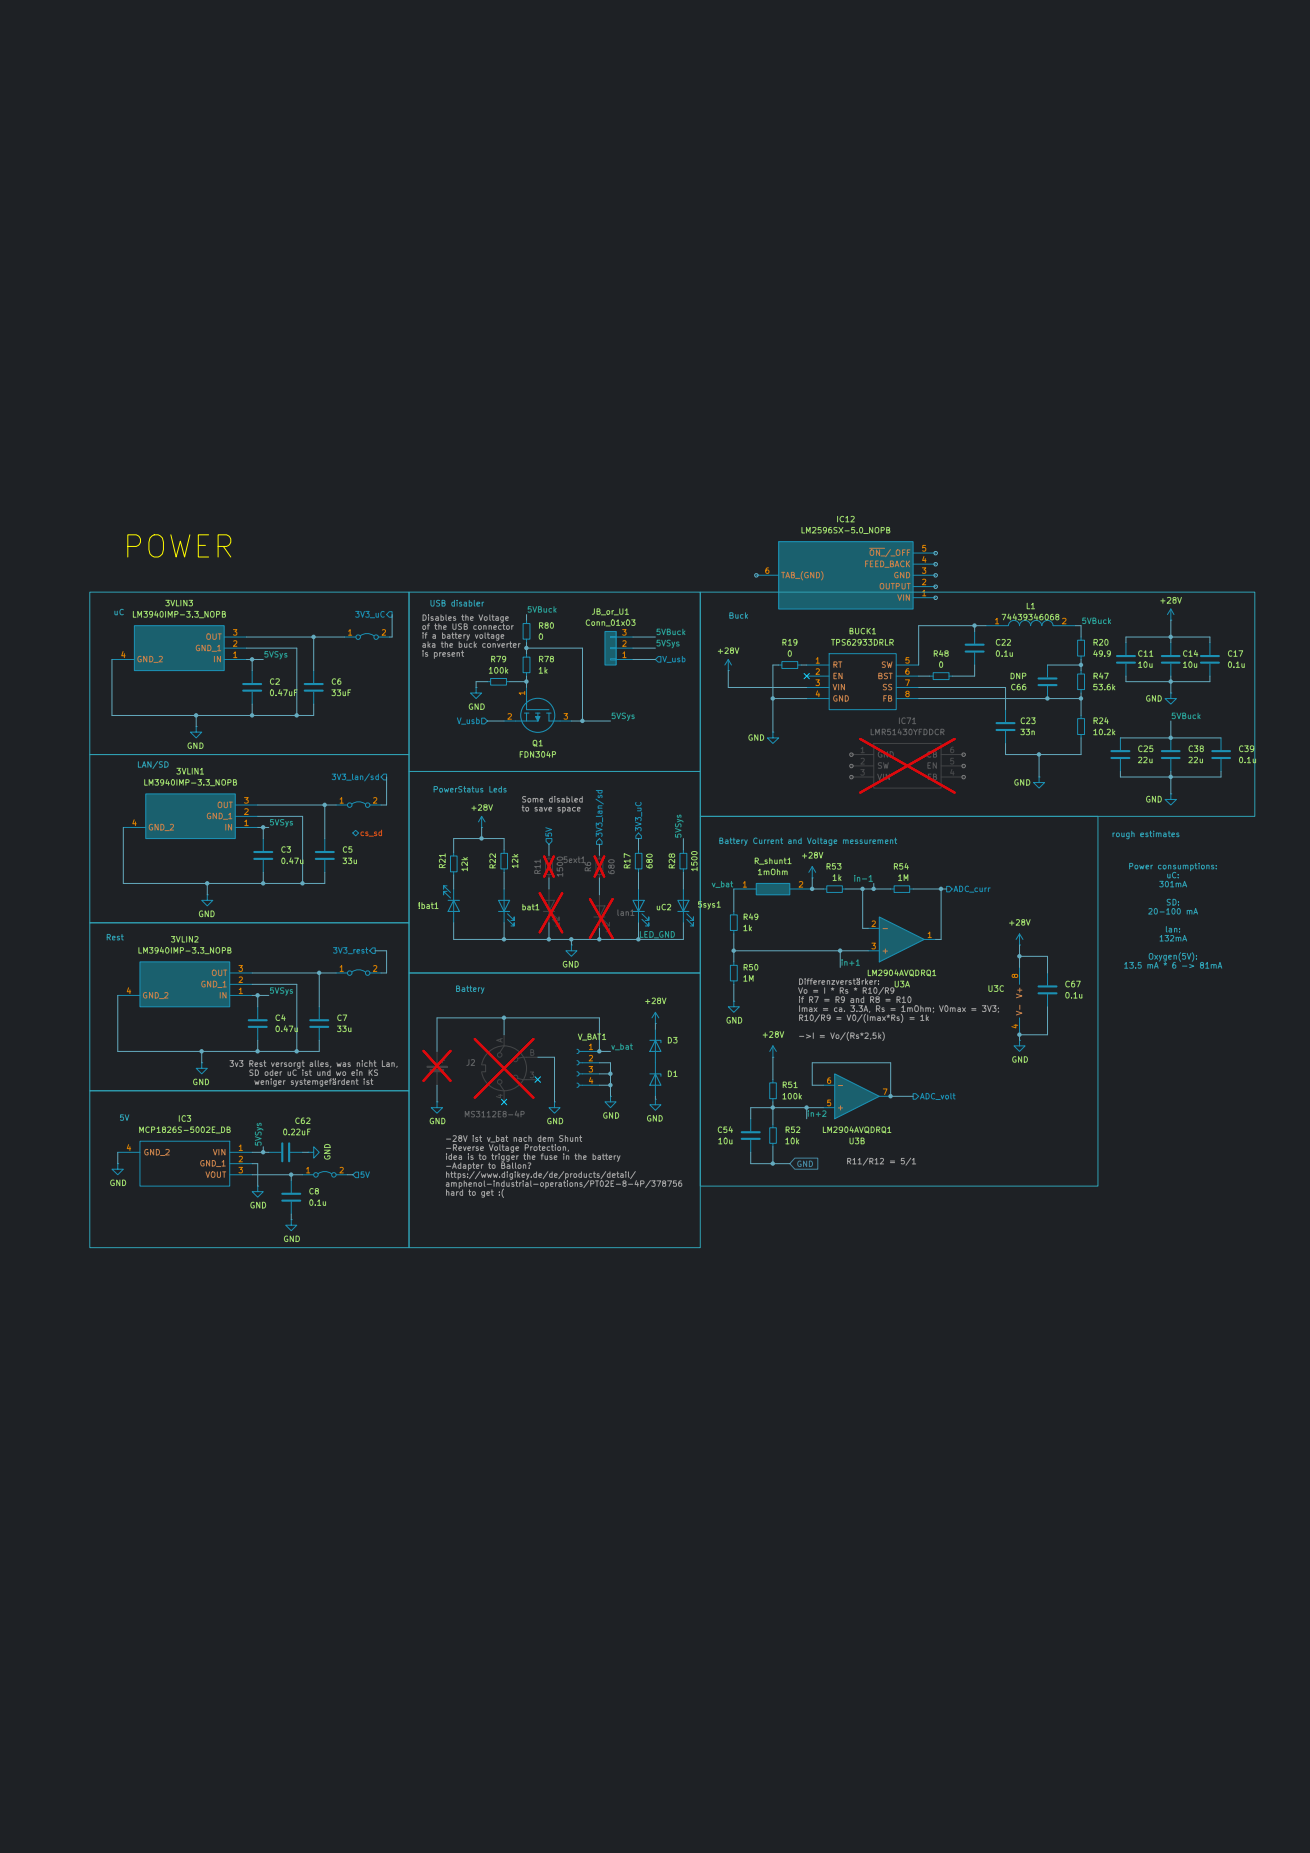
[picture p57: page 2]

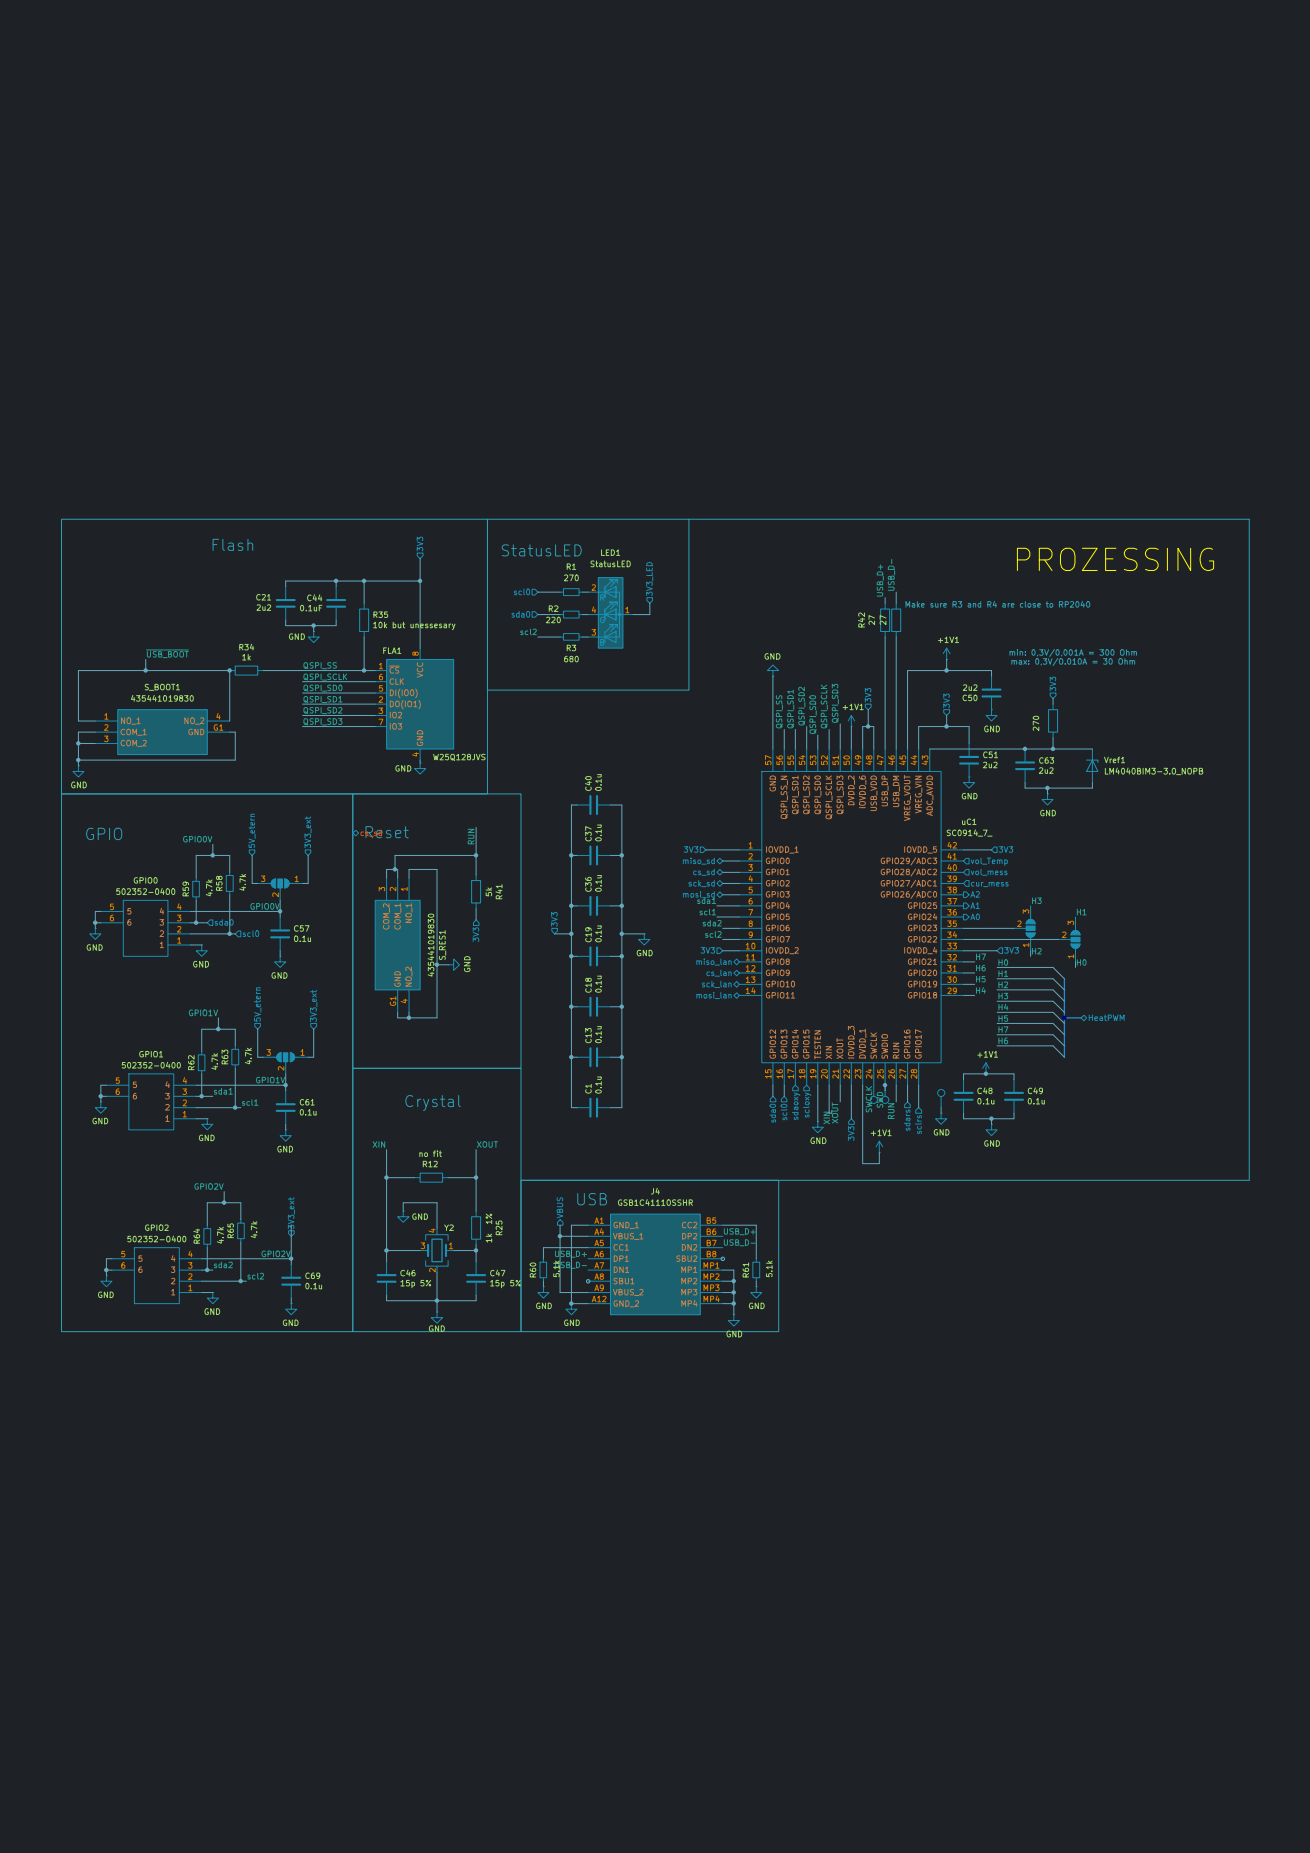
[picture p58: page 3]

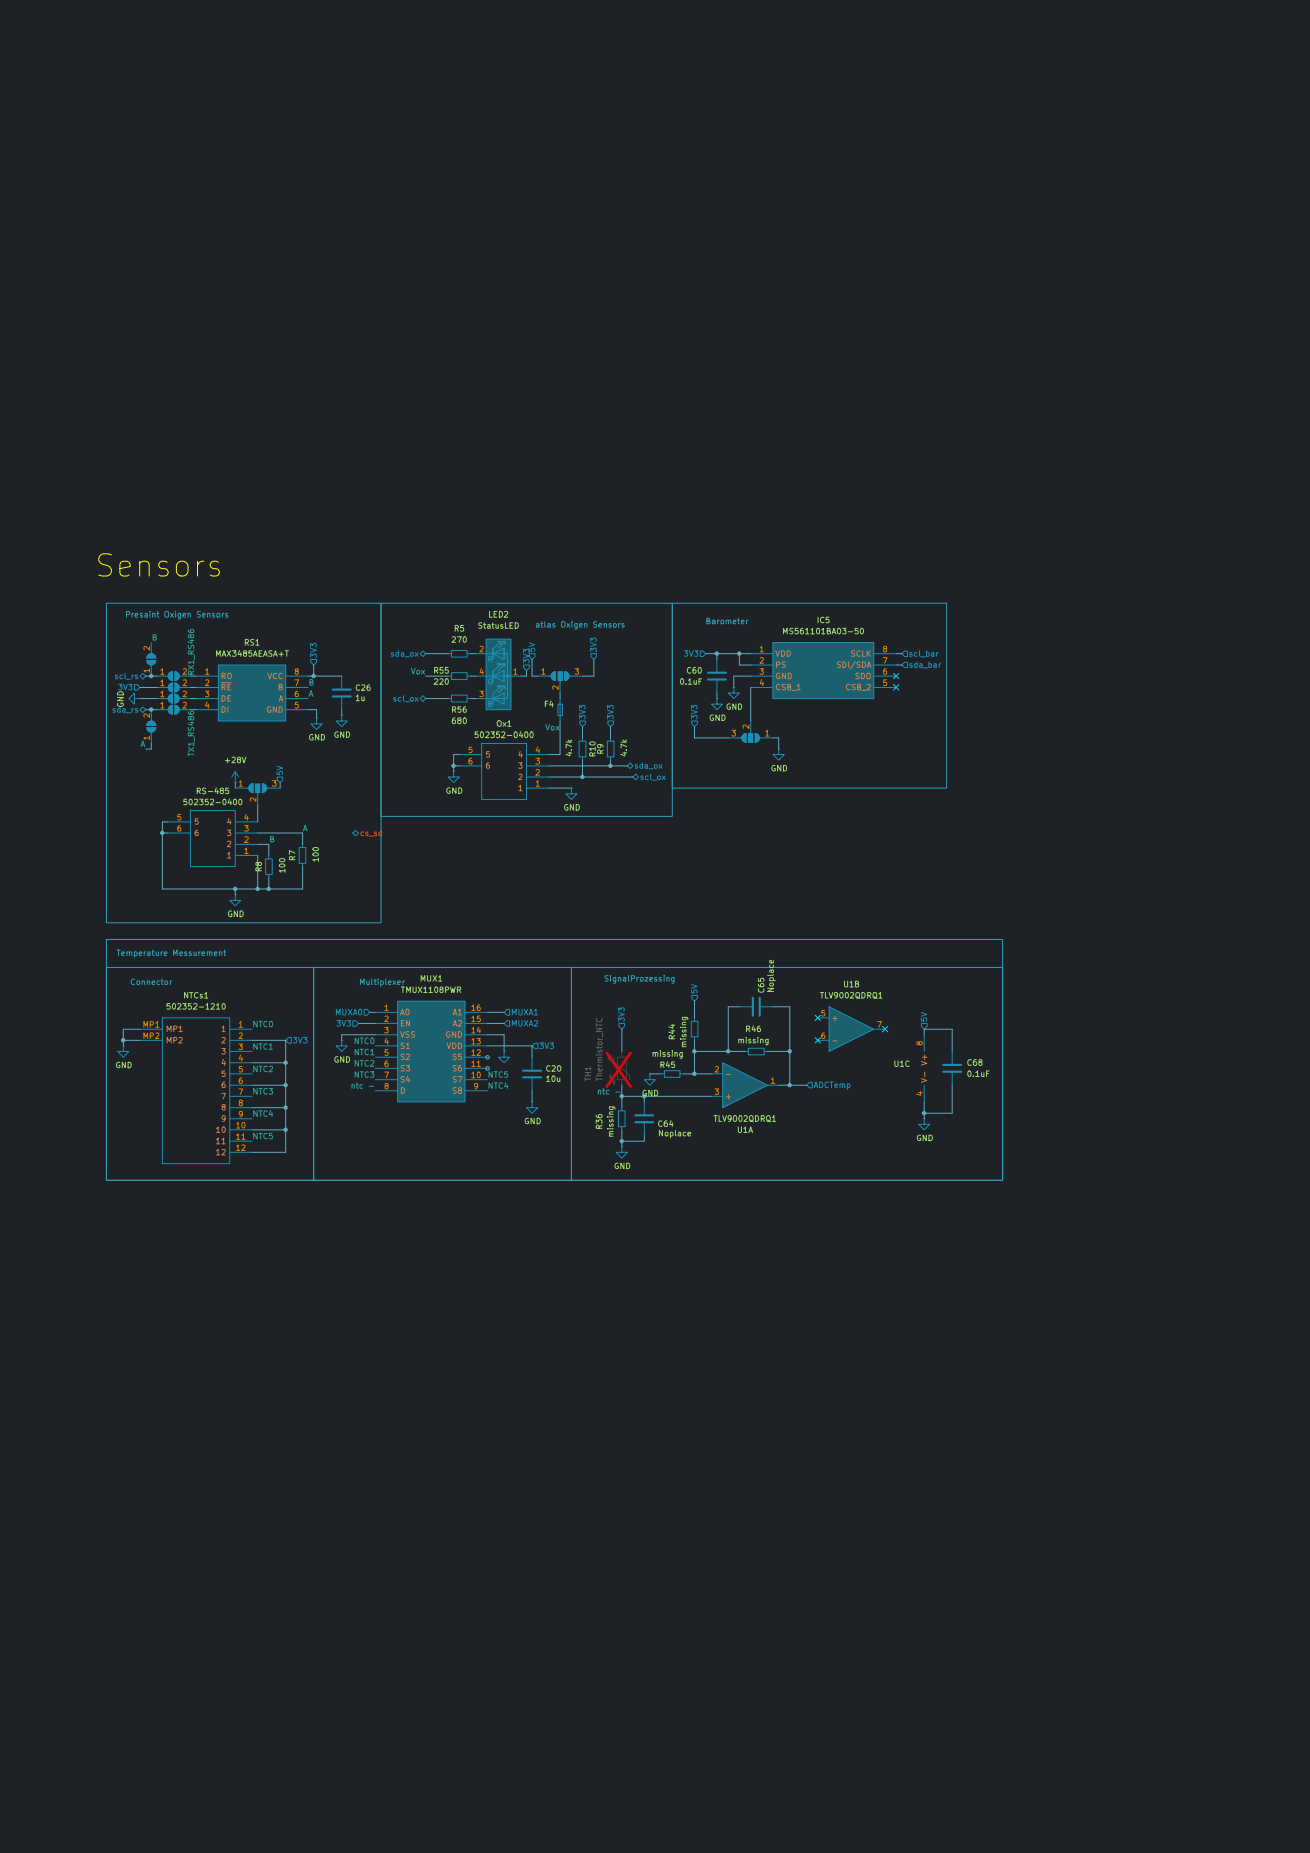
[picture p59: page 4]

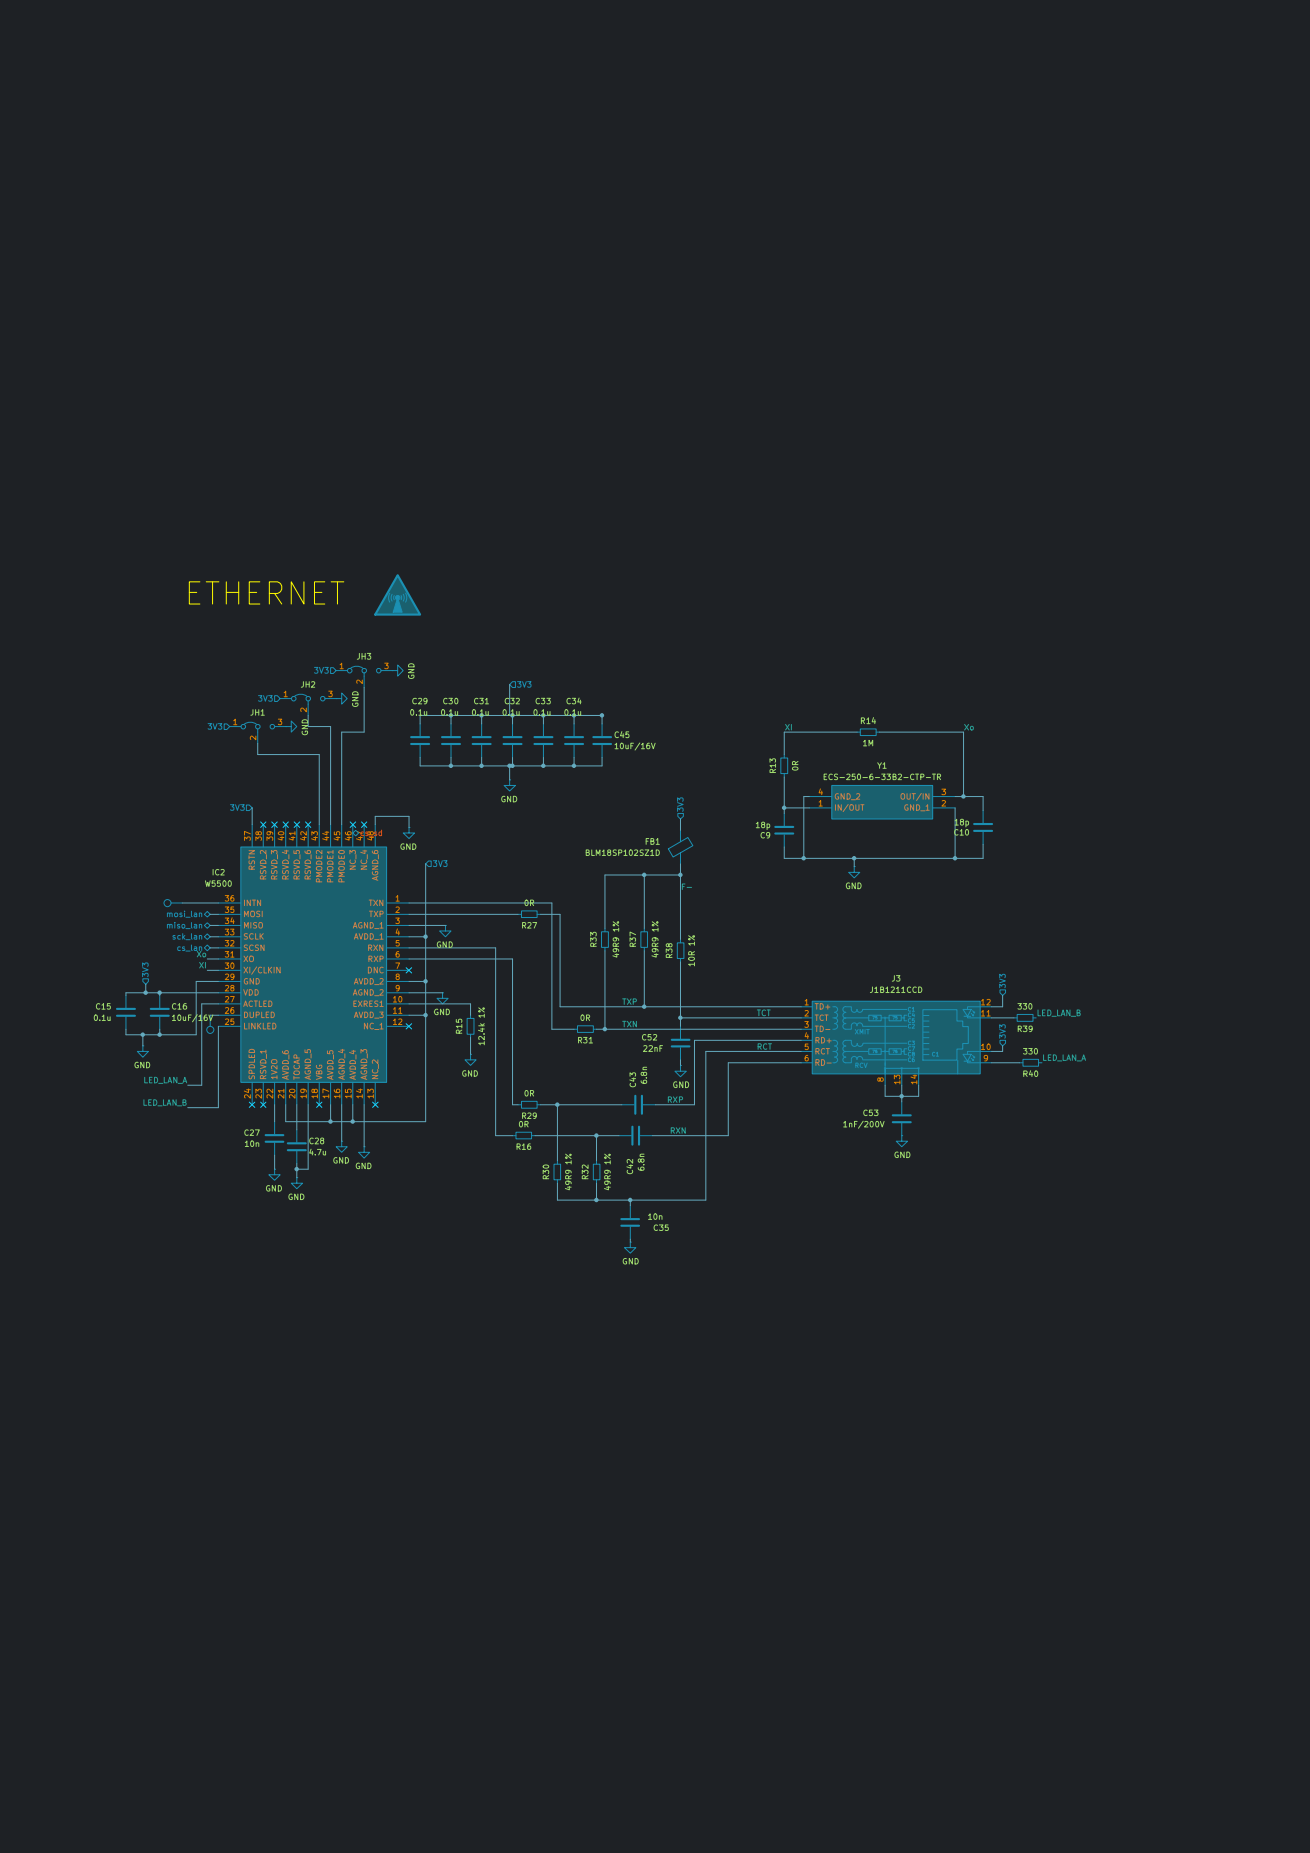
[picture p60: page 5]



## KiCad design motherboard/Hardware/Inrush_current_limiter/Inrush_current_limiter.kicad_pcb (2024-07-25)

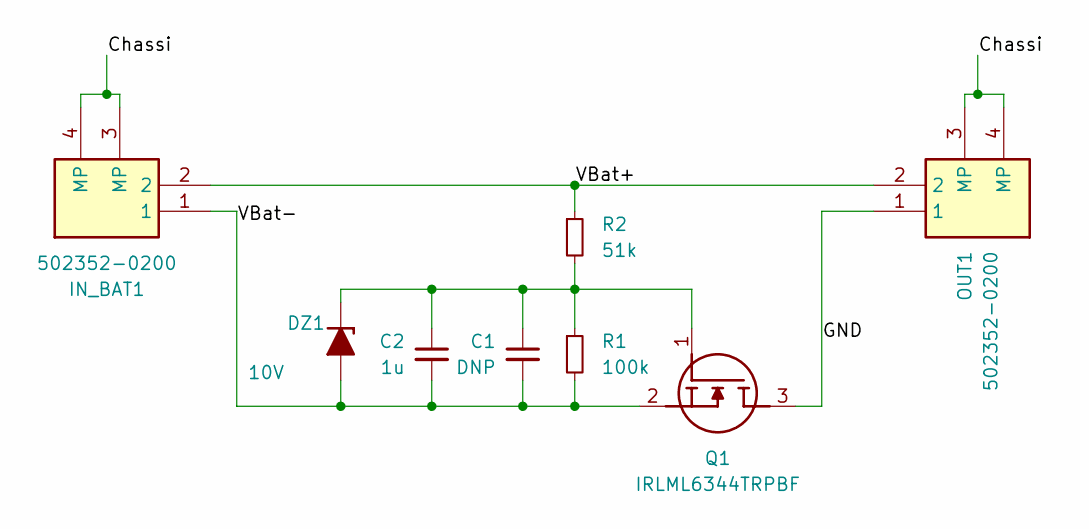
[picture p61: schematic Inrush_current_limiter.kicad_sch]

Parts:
C1: DNP; C_0603_1608Metric_Pad1.08x0.95mm_HandSolder
C2: 1u; C_0603_1608Metric_Pad1.08x0.95mm_HandSolder
DZ1: 10V; D_A-405_P2.54mm_Vertical_KathodeUp
IN_BAT1: 502352-0200; 5023520200; Mouser Part Number 538-502352-0200
OUT1: 502352-0200; 5023520200; Mouser Part Number 538-502352-0200
Q1: IRLML6344TRPBF; SOT95P237X112-3N; Mouser Part Number 942-IRLML6344TRPBF
R1: 100k; R_0603_1608Metric_Pad0.98x0.95mm_HandSolder
R2: 51k; R_0603_1608Metric_Pad0.98x0.95mm_HandSolder

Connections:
/Chassi: IN_BAT1.3 (MP), IN_BAT1.4 (MP), OUT1.3 (MP), OUT1.4 (MP)
/GND: OUT1.1, Q1.3 (D)
/VBat+: IN_BAT1.2, OUT1.2, R2.1
/VBat-: C1.2, C2.2, DZ1.2 (A), IN_BAT1.1, Q1.2 (S), R1.2
unnamed: C1.1, C2.1, DZ1.1 (K), Q1.1 (G), R1.1, R2.2

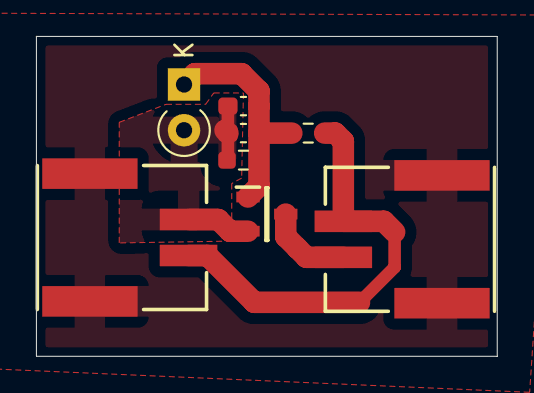
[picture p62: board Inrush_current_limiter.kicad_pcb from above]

Board: 2 copper layers, 25.6 x 17.8 mm, 8 parts (0 on the bottom side), 5 nets.

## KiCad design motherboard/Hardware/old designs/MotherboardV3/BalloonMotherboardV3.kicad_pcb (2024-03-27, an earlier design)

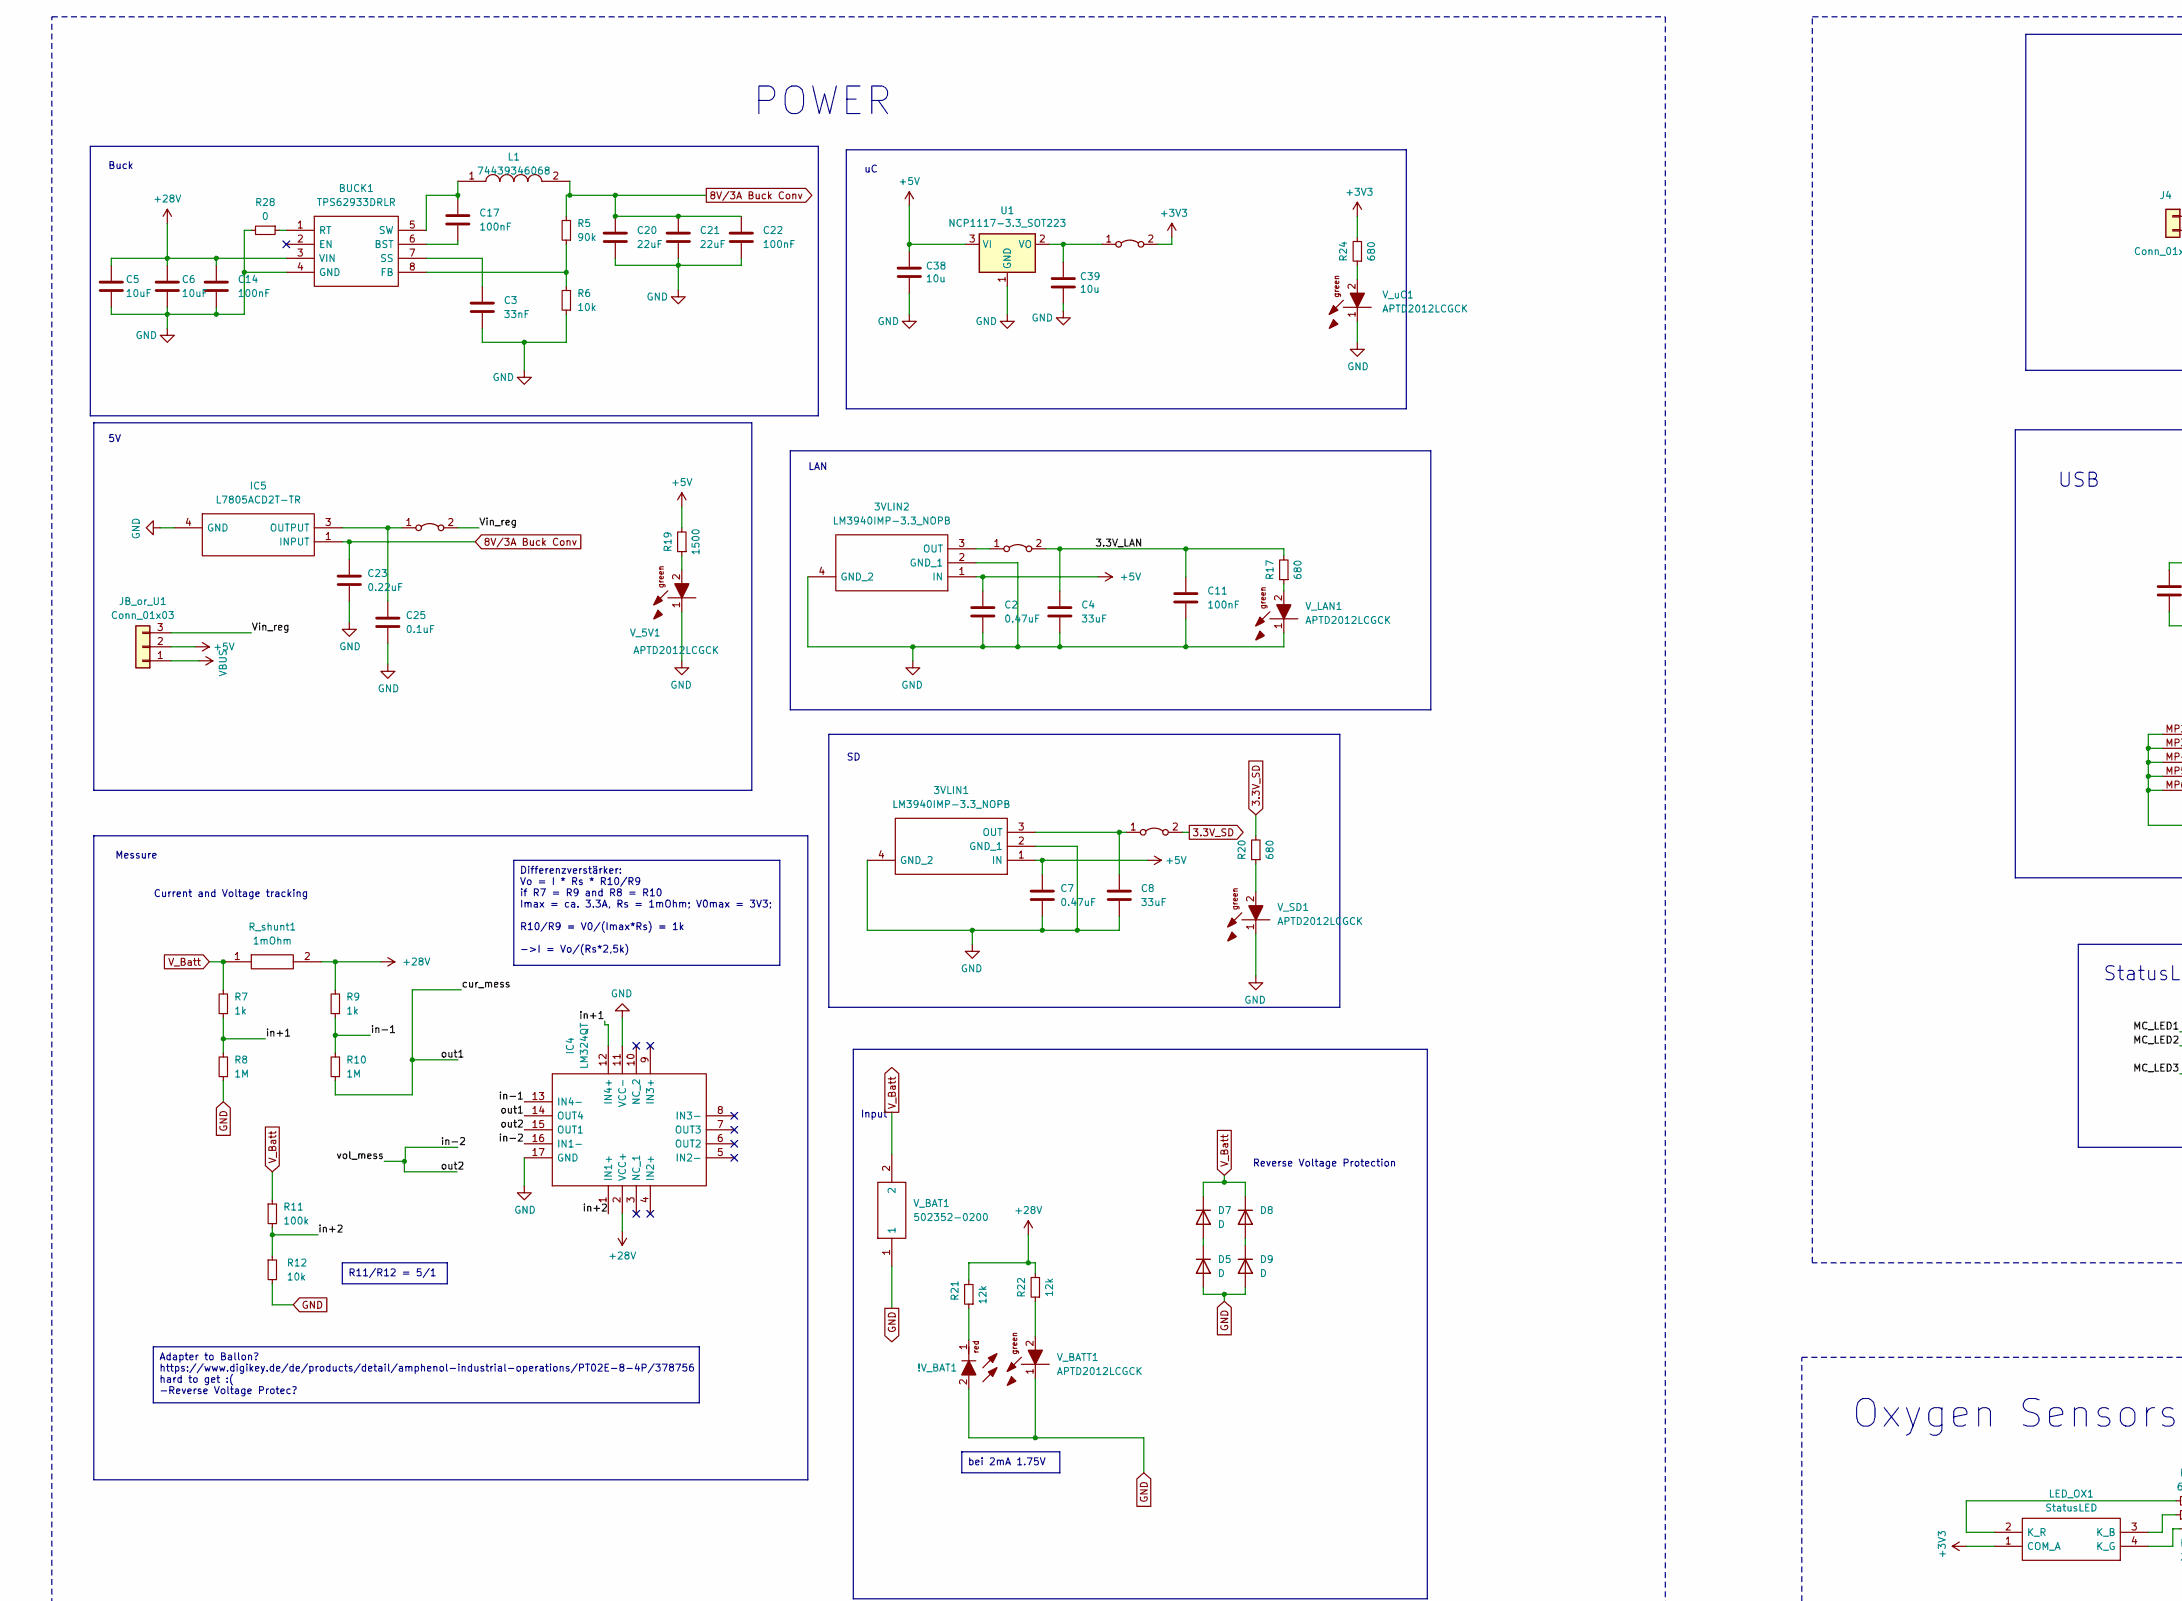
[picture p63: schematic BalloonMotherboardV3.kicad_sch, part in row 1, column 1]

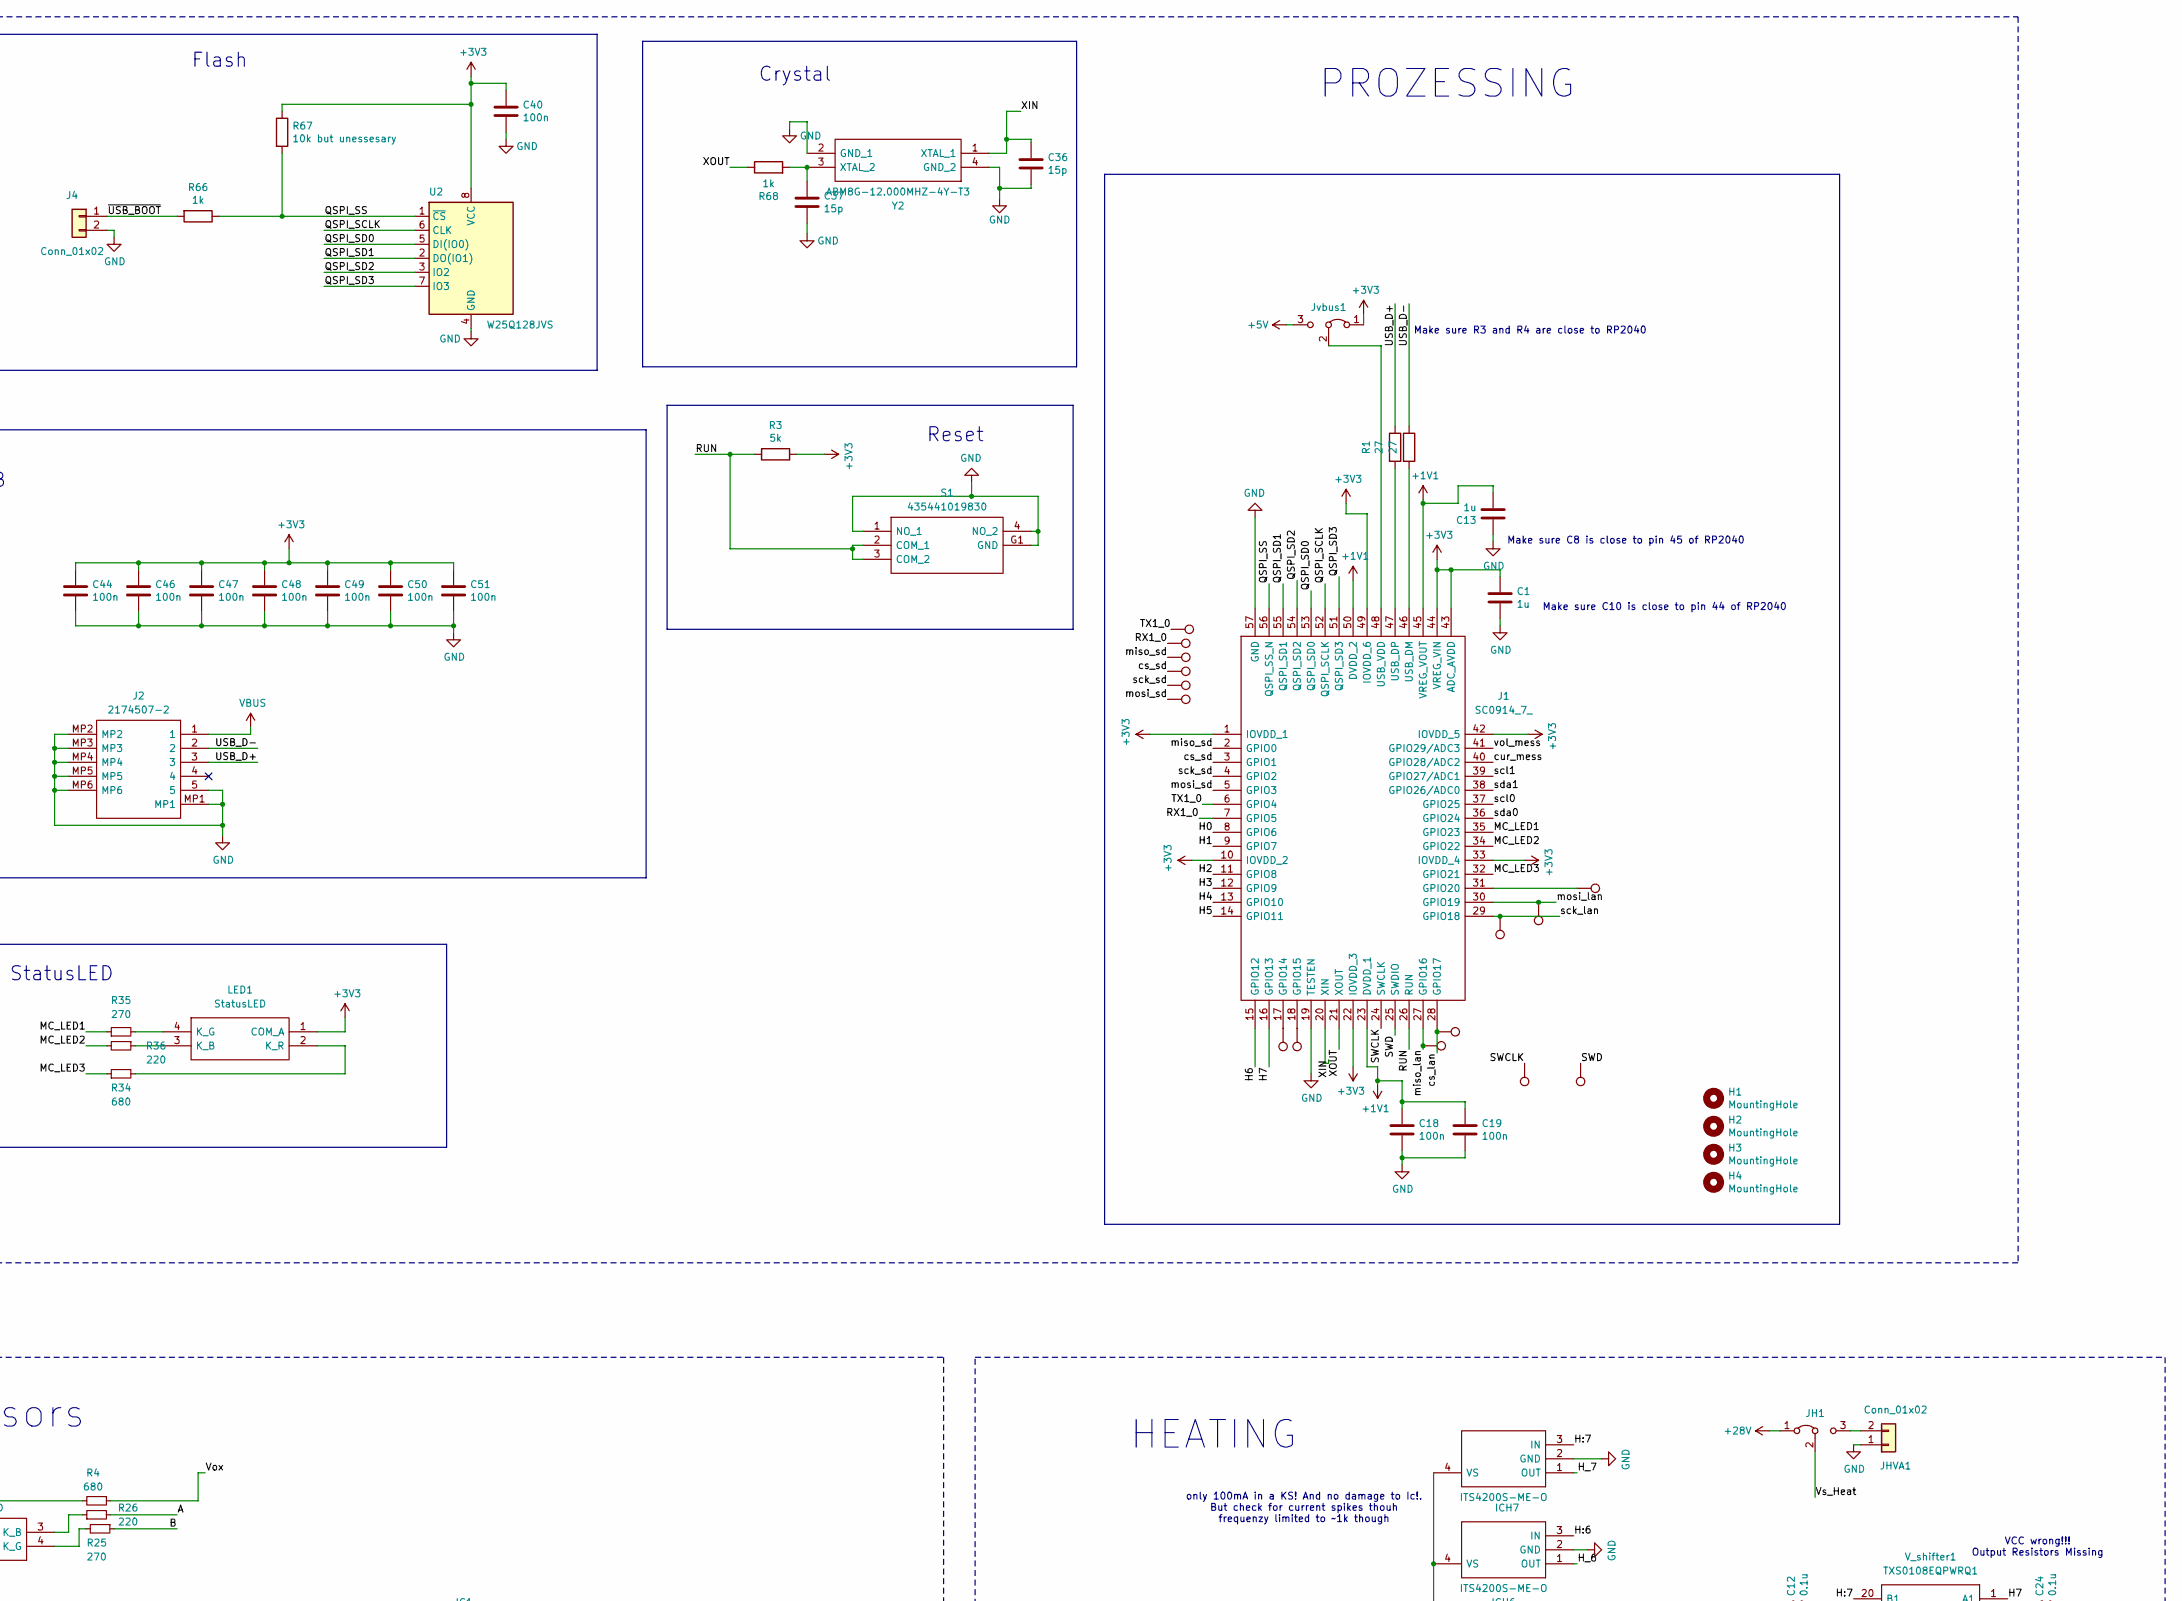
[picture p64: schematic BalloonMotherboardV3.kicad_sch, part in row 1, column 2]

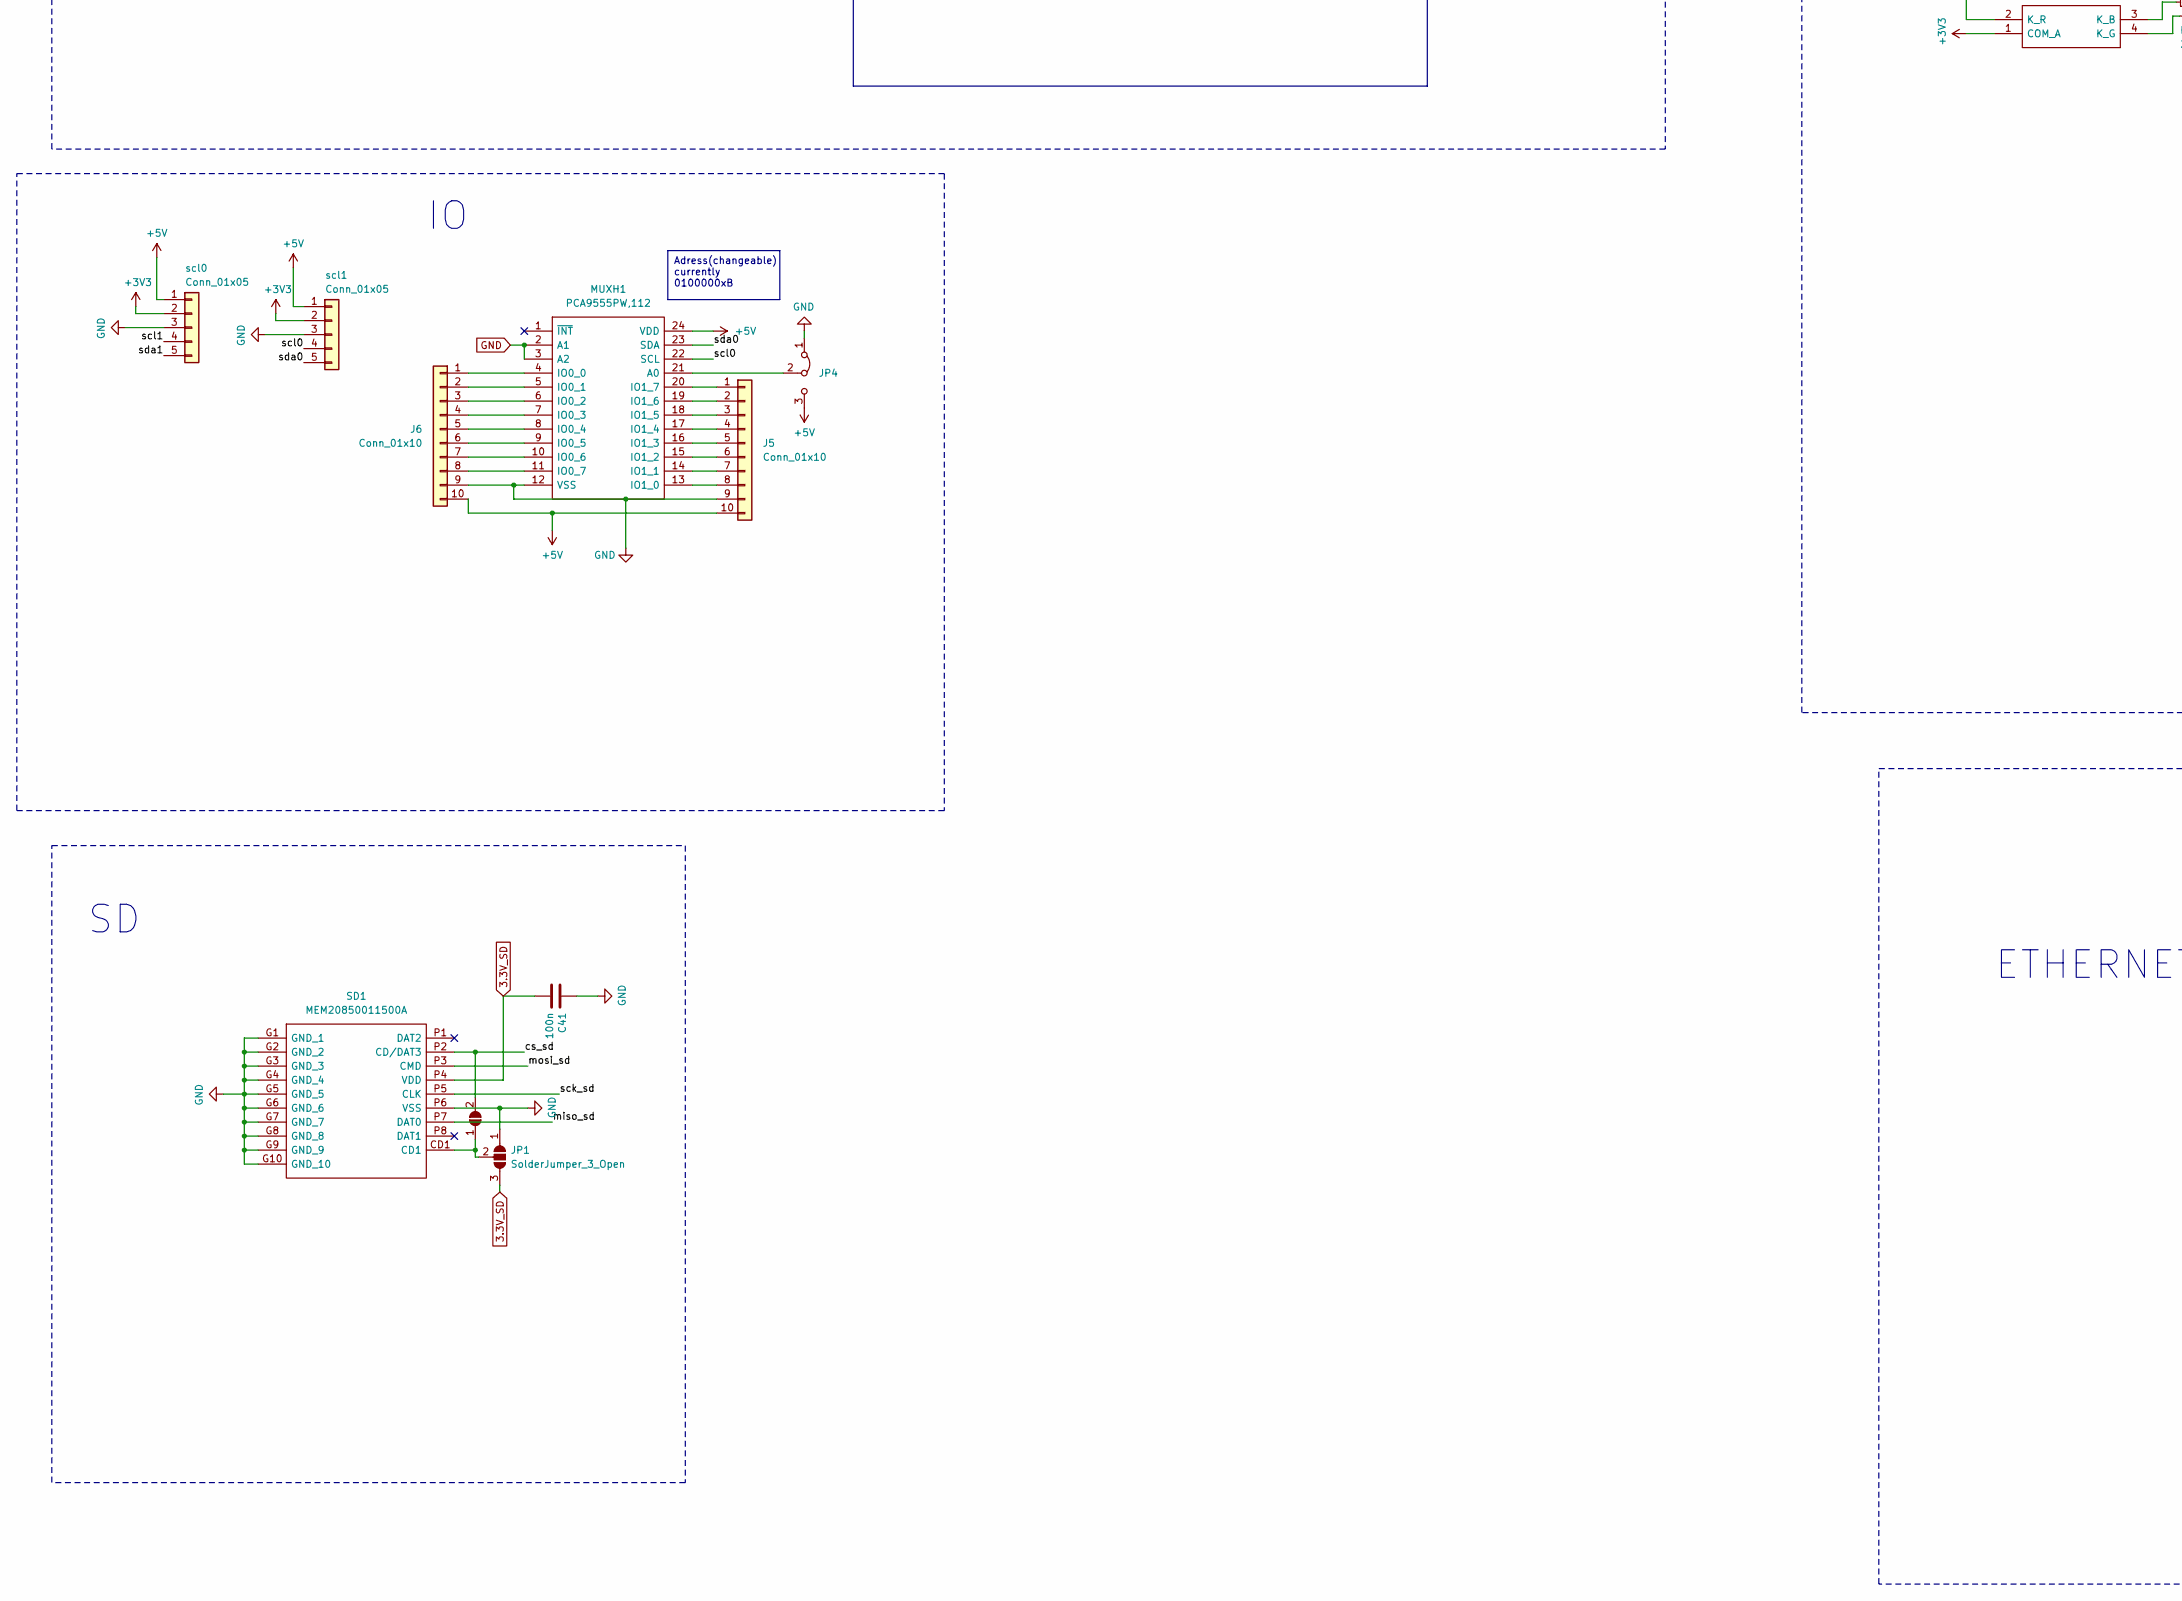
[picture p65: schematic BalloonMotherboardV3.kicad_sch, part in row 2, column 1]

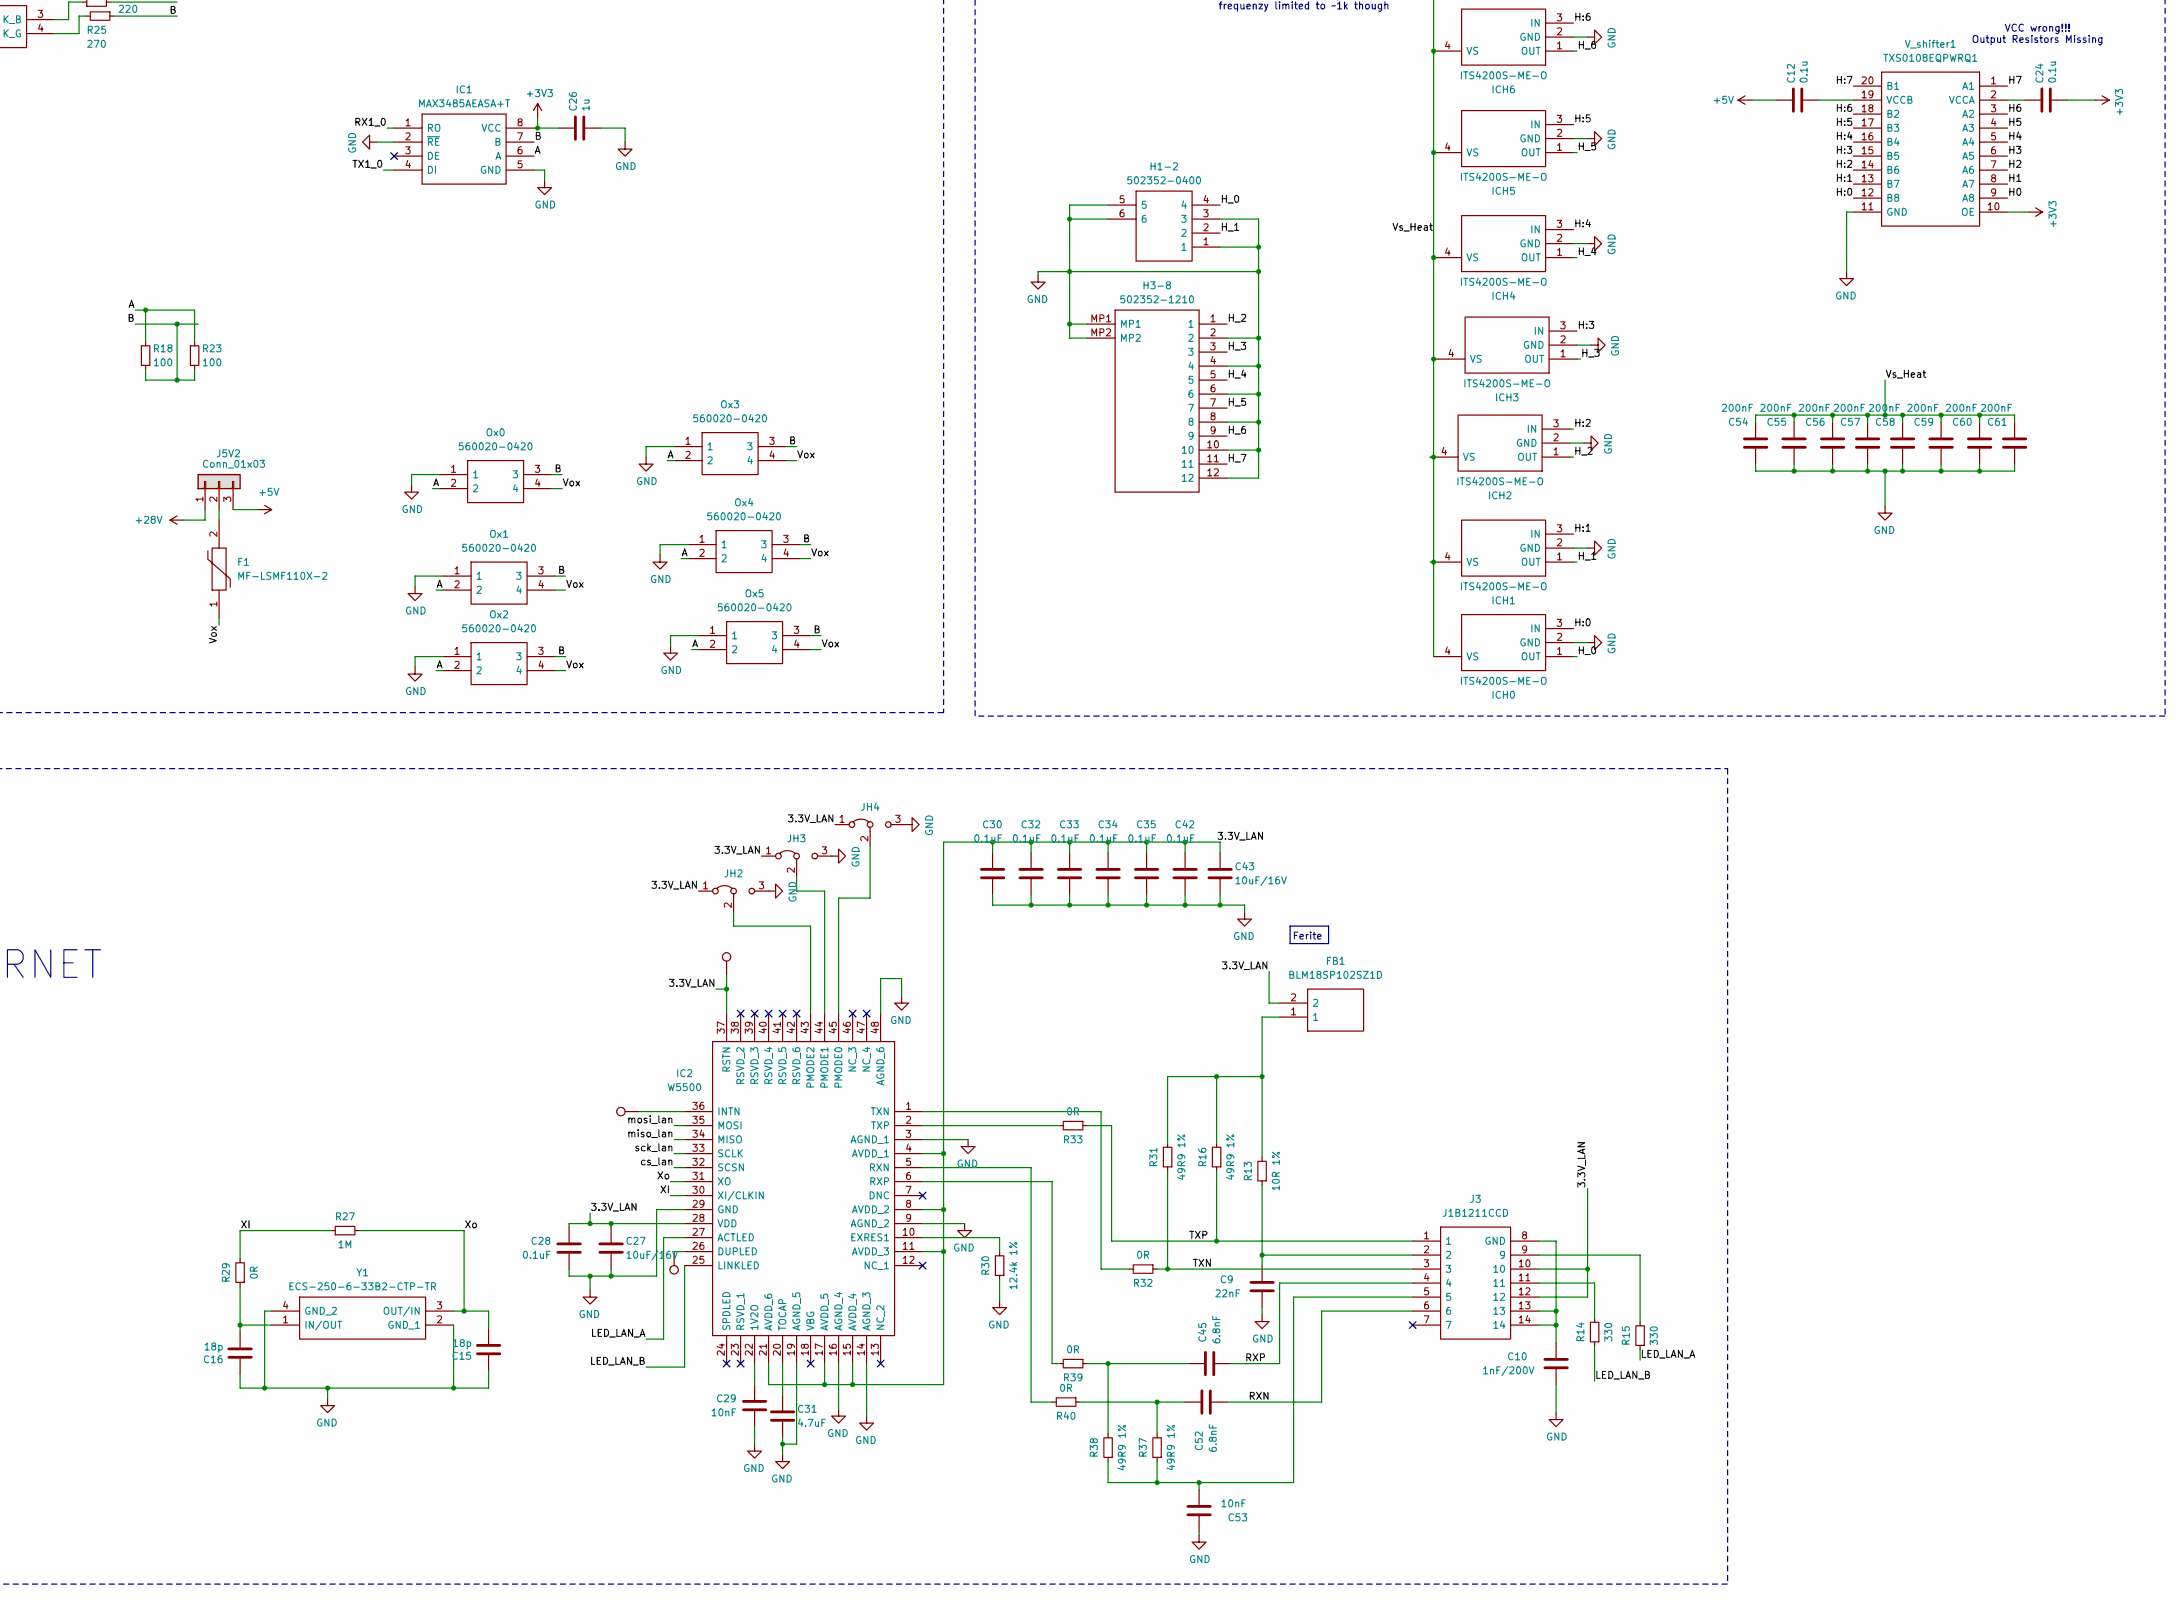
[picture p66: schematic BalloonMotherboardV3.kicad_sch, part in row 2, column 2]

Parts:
3VLIN1, 3VLIN2: LM3940IMP-3.3_NOPB; SOT230P700X180-4N; Mouser Part Number 926-LM3940IMP3.3NOPB
!V_BAT1: APTD2012LSURCK; LEDM2012X120N; Mouser Part Number 604-APTD2012LSURCK
BUCK1: TPS62933DRLR; SOTFL50P160X60-8N; Mouser Part Number 595-TPS62933DRLR
C1, C13: 1u; C_0402_1005Metric
C2, C7: 0.47uF; C_0603_1608Metric
C3: 33nF; C_0603_1608Metric
C4, C8: 33uF; C_0603_1608Metric
C5, C6: 10uF; C_1206_3216Metric_Pad1.33x1.80mm_HandSolder
C9: 22nF; C_0402_1005Metric
C10: 1nF/200V; C_0402_1005Metric
C11, C14, C17, C22: 100nF; C_0603_1608Metric
C12, C24: 0.1u; C_0402_1005Metric
C15, C16: 18p; C_0402_1005Metric
C18, C19, C40, C41, C44, C46, C47, C48, C49, C50, C51: 100n; C_0402_1005Metric
C20, C21: 22uF; C_0603_1608Metric
C23: 0.22uF; C_0603_1608Metric
C25: 0.1uF; C_0603_1608Metric
C26: 1u; C_0805_2012Metric
C27, C43: 10uF/16V; C_1206_3216Metric_Pad1.33x1.80mm_HandSolder
C28, C30, C32, C33, C34, C35, C42: 0.1uF; C_0402_1005Metric
C29, C53: 10nF; C_0402_1005Metric
C31: 4.7uF; C_1206_3216Metric_Pad1.33x1.80mm_HandSolder
C36, C37: 15p; C_0402_1005Metric
C38, C39: 10u; C_0805_2012Metric
C45, C52: 6.8nF; C_0402_1005Metric
C54, C55, C56, C57, C58, C59, C60, C61: 200nF; C_0402_1005Metric
D5, D7, D9: D; DIOM5336X245N
D8: RBR2LB60BTBR1; DIOM5336X245N
F1: MF-LSMF110X-2; MFLSMF110X2; Mouser Part Number 652-MF-LSMF110X-2
FB1: BLM18SP102SZ1D; BLM18SP221SN1B; Mouser Part Number 81-BLM18SP102SZ1D
H1, H2, H3, H4: MountingHole; MountingHole_3.2mm_M3_DIN965_Pad_TopBottom
H1-2: 502352-0400; 5023520400; Mouser Part Number 538-502352-0400
H3-8: 502352-1210; 5023521210; Mouser Part Number 538-502352-1210
IC1: MAX3485AEASA+T; SOIC127P600X175-8N; Mouser Part Number 700-MAX3485AEASA+T
IC2: W5500; QFP50P900X900X160-48N; Mouser Part Number 950-W5500
IC4: LM324QT; QFN50P300X300X100-17N; Mouser Part Number 511-LM324QT
IC5: L7805ACD2T-TR; D2PAK-STB35NF10T4; Mouser Part Number 511-L7805ACD2T-TR
ICH0, ICH1, ICH2, ICH3, ICH4, ICH5, ICH6, ICH7: ITS4200S-ME-O; SOT230P700X170-4N; Mouser Part Number 726-ITS4200S-ME-O
J1: SC0914_7_; QFN40P700X700X90-57N-D; Mouser Part Number 358-SC09147
J2: 2174507-2; 21745072; Mouser Part Number 571-2174507-2
J3: J1B1211CCD; Mouser Part Number 950-J1B1211CCD
J4: Conn_01x02; PinHeader_1x02_P2.54mm_Vertical
J5, J6: Conn_01x10; PinHeader_1x10_P2.54mm_Vertical
J5V2: Conn_01x03; PinHeader_1x03_P2.54mm_Vertical
JB_or_U1: Conn_01x03; PinHeader_1x03_P2.54mm_Vertical
JH1, JH2, JH3, JH4: Jumper_3_Bridged12; SolderJumper-3_P1.3mm_Bridged12_RoundedPad1.0x1.5mm_NumberL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
JHVA1: Conn_01x02; PinHeader_1x02_P2.54mm_Vertical
JP1: SolderJumper_3_Open; SolderJumper-3_P1.3mm_Open_RoundedPad1.0x1.5mm_NumberLabels
JP3, JP5, JP9, JP10: Jumper_2_Bridged; SolderJumper-2_P1.3mm_Bridged2Bar_RoundedPad1.0x1.5mm
JP4: Jumper_3_Bridged12; SolderJumper-3_P1.3mm_Bridged12_RoundedPad1.0x1.5mm_NumberL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
JP11: SolderJumper_2_Open; SolderJumper-2_P1.3mm_Open_Pad1.0x1.5mm
Jvbus1: Jumper_3_Bridged12; SolderJumper-3_P1.3mm_Bridged12_RoundedPad1.0x1.5mm_NumberL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
L1: 74439346068; Mouser Part Number 710-74439346068
LED1: StatusLED; LTRBR37G4R4S01250; Mouser Part Number 720-LTRBR37GA6714
LED_OX1: StatusLED; LTRBR37G4R4S01250; Mouser Part Number 720-LTRBR37GA6714
MUXH1: PCA9555PW,112; SOP65P640X110-24N; Mouser Part Number 771-PCA9555PW
Ox0, Ox1, Ox2, Ox3, Ox4, Ox5: 560020-0420; Mouser Part Number 538-560020-0420
R1, R2: 27; R_0402_1005Metric
R3: 5k; R_0402_1005Metric
R4, R17, R20, R24, R34: 680; R_0805_2012Metric_Pad1.20x1.40mm_HandSolder
R5: 90k; R_0603_1608Metric
R6: 10k; R_0603_1608Metric
R7, R9: 1k; R_0805_2012Metric_Pad1.20x1.40mm_HandSolder
R8, R10: 1M; R_0805_2012Metric_Pad1.20x1.40mm_HandSolder
R11: 100k; R_0805_2012Metric_Pad1.20x1.40mm_HandSolder
R12: 10k; R_0402_1005Metric
R13: 10R 1%; R_0402_1005Metric
R14, R15: 330; R_0402_1005Metric
R16, R31, R37, R38: 49R9 1%; R_0402_1005Metric
R18, R23: 100; R_0805_2012Metric_Pad1.20x1.40mm_HandSolder
R19: 1500; R_0805_2012Metric_Pad1.20x1.40mm_HandSolder
R21, R22: 12k; R_0805_2012Metric_Pad1.20x1.40mm_HandSolder
R25, R35: 270; R_0805_2012Metric_Pad1.20x1.40mm_HandSolder
R26, R36: 220; R_0805_2012Metric_Pad1.20x1.40mm_HandSolder
R27: 1M; R_0402_1005Metric
R28: 0; R_0603_1608Metric
R29, R32, R33, R39, R40: 0R; R_0402_1005Metric
R30: 12.4k 1%; R_0402_1005Metric
R66, R68: 1k; R_0402_1005Metric
R67: 10k but unessesary; R_0402_1005Metric
R_shunt1: 1mOhm; RESC3216X90N; Mouser Part Number 603-PA1206FRE7W0R01Z
S1: 435441019830; Mouser Part Number 710-435441019830
SD1: MEM20850011500A; Mouser Part Number 640-MEM20850011500A
TP1, TP2, TP3, TP4, TP5, TP6, TP7, TP8, TP9, TP10, TP11, TP12, TP13, TP14, TP15, TP16, TP17, TP18: TestPoint; TestPoint_Pad_D1.0mm
U1: NCP1117-3.3_SOT223; SOT-223-3_TabPin2
U2: W25Q128JVS; SOIC-8_5.23x5.23mm_P1.27mm
V_5V1: APTD2012LCGCK; LEDC2012X120N; Mouser Part Number 604-APTD2012LCGCK
V_BAT1: 502352-0200; 5023520200; Mouser Part Number 538-502352-0200
V_BATT1: APTD2012LCGCK; LEDC2012X120N; Mouser Part Number 604-APTD2012LCGCK
V_LAN1: APTD2012LCGCK; LEDC2012X120N; Mouser Part Number 604-APTD2012LCGCK
V_SD1: APTD2012LCGCK; LEDC2012X120N; Mouser Part Number 604-APTD2012LCGCK
V_shifter1: TXS0108EQPWRQ1; SOP65P640X120-20N; Mouser Part Number 595-TXS0108EQPWRQ1
V_uC1: APTD2012LCGCK; LEDC2012X120N; Mouser Part Number 604-APTD2012LCGCK
Y1: ECS-250-6-33B2-CTP-TR; ECS250633B2CTPTR; Mouser Part Number 520-250-6-33B2-CTPTR
Y2: ABM8G-12.000MHZ-4Y-T3; ABM8G; Mouser Part Number 815-ABM8G-12-4YT3
scl0, scl1: Conn_01x05; PinHeader_1x05_P2.54mm_Vertical

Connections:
3.3V_SD: C41.2, JP1.3 (B), JP9.2 (B), R20.2, SD1.P4 (VDD)
8V/3A Buck Conv: C20.2, C21.2, C22.2, C23.2, IC5.1 (INPUT), L1.2, R5.2
+1V1: C13.2, C18.1, C19.1, J1.23 (DVDD_1), J1.45 (VREG_VOUT), J1.50 (DVDD_2)
+3V3: C1.1, C24.2, C26.1, C40.1, C44.1, C46.1, C47.1, C48.1, C49.1, C50.1, C51.1, IC1.8 (VCC), J1.1 (IOVDD_1), J1.10 (IOVDD_2), J1.22 (IOVDD_3), J1.33 (IOVDD_4), J1.42 (IOVDD_5), J1.43 (ADC_AVDD), J1.44 (VREG_VIN), J1.49 (IOVDD_6), JP10.2 (B), Jvbus1.1 (A), LED1.1 (COM_A), LED_OX1.1 (COM_A), R3.1, R24.2, R67.1, U2.8 (VCC), V_shifter1.10 (OE), scl0.2, scl1.2
+5V: 3VLIN1.1 (IN), 3VLIN2.1 (IN), C2.2, C7.2, C12.1, C38.1, J5.10, J5V2.3, J6.10, JB_or_U1.2, JP4.3 (B), Jvbus1.3 (B), MUXH1.24 (VDD), R19.2, U1.3 (VI), scl0.1, scl1.1
+28V: BUCK1.3 (VIN), C5.2, C6.2, C14.2, IC4.2 (VCC+), J5V2.1, JH1.1 (A), R9.2, R21.2, R22.2, R_shunt1.2
/3.3V_LAN: C4.2, C11.2, C27.2, C28.2, C30.2, C32.2, C33.2, C34.2, C35.2, C42.2, C43.2, FB1.2, IC2.4 (AVDD_1), IC2.8 (AVDD_2), IC2.11 (AVDD_3), IC2.15 (AVDD_4), IC2.17 (AVDD_5), IC2.21 (AVDD_6), IC2.28 (VDD), IC2.37 (RSTN), J3.10, J3.12, JH2.1 (A), JH3.1 (A), JH4.1 (A), JP3.2 (B), R17.2, TP17.1
/A: IC1.6 (A), Ox0.2, Ox1.2, Ox2.2, Ox3.2, Ox4.2, Ox5.2, R18.1, R23.1, R26.2
/B: IC1.7 (B), Ox0.3, Ox1.3, Ox2.3, Ox3.3, Ox4.3, Ox5.3, R18.2, R23.2, R25.1
/H0: J1.8 (GPIO6), V_shifter1.9 (A8)
/H1: J1.9 (GPIO7), V_shifter1.8 (A7)
/H2: J1.11 (GPIO8), V_shifter1.7 (A6)
/H3: J1.12 (GPIO9), V_shifter1.6 (A5)
/H4: J1.13 (GPIO10), V_shifter1.5 (A4)
/H5: J1.14 (GPIO11), V_shifter1.4 (A3)
/H6: J1.15 (GPIO12), V_shifter1.3 (A2)
/H7: J1.16 (GPIO13), V_shifter1.1 (A1)
/H:0: ICH0.3 (IN), V_shifter1.12 (B8)
/H:1: ICH1.3 (IN), V_shifter1.13 (B7)
/H:2: ICH2.3 (IN), V_shifter1.14 (B6)
/H:3: ICH3.3 (IN), V_shifter1.15 (B5)
/H:4: ICH4.3 (IN), V_shifter1.16 (B4)
/H:5: ICH5.3 (IN), V_shifter1.17 (B3)
/H:6: ICH6.3 (IN), V_shifter1.18 (B2)
/H:7: ICH7.3 (IN), V_shifter1.20 (B1)
/H_0: H1-2.4, ICH0.1 (OUT)
/H_1: H1-2.2, ICH1.1 (OUT)
/H_2: H3-8.1, ICH2.1 (OUT)
/H_3: H3-8.3, ICH3.1 (OUT)
/H_4: H3-8.5, ICH4.1 (OUT)
/H_5: H3-8.7, ICH5.1 (OUT)
/H_6: H3-8.9, ICH6.1 (OUT)
/H_7: H3-8.11, ICH7.1 (OUT)
/LED_LAN_A: IC2.27 (ACTLED), R15.1
/LED_LAN_B: IC2.25 (LINKLED), R14.1
/MC_LED1: J1.35 (GPIO23), R35.1
/MC_LED2: J1.34 (GPIO22), R36.2
/MC_LED3: J1.32 (GPIO21), R34.1
/QSPI_SCLK: J1.52 (QSPI_SCLK), U2.6 (CLK)
/QSPI_SD0: J1.53 (QSPI_SD0), U2.5 (DI(IO0))
/QSPI_SD1: J1.55 (QSPI_SD1), U2.2 (DO(IO1))
/QSPI_SD2: J1.54 (QSPI_SD2), U2.3 (IO2)
/QSPI_SD3: J1.51 (QSPI_SD3), U2.7 (IO3)
/QSPI_SS: J1.56 (QSPI_SS_N), R66.1, R67.2, U2.1 (~CS)
/RUN: J1.26 (RUN), R3.2, S1.2 (COM_1), S1.3 (COM_2)
/RX1_0: IC1.1 (RO), J1.7 (GPIO5), TP11.1
/RXN: C52.1, J3.6
/RXP: C45.1, J3.4
/SWCLK: J1.24 (SWCLK), TP12.1
/SWD: J1.25 (SWDIO), TP1.1
/TX1_0: IC1.4 (DI), J1.6 (GPIO4), TP10.1
/TXN: J3.3, R31.1, R32.1
/TXP: J3.1, R16.1, R33.1
/USB_D+: J2.3, R1.1
/USB_D-: J2.2, R2.1
/Vin_reg: JB_or_U1.3, JP5.2 (B)
/Vox: F1.1, Ox0.4, Ox1.4, Ox2.4, Ox3.4, Ox4.4, Ox5.4, R4.1
/Vs_Heat: C54.1, C55.1, C56.1, C57.1, C58.1, C59.1, C60.1, C61.1, ICH0.4 (VS), ICH1.4 (VS), ICH2.4 (VS), ICH3.4 (VS), ICH4.4 (VS), ICH5.4 (VS), ICH6.4 (VS), ICH7.4 (VS), JH1.2 (C)
/XI: IC2.30 (XI/CLKIN), R27.1, R29.2
/XIN: C36.1, J1.20 (XIN), Y2.1 (XTAL_1)
/XOUT: J1.21 (XOUT), R68.1
/Xo: C15.2, IC2.31 (XO), R27.2, Y1.3 (OUT/IN)
/cs_lan: IC2.32 (SCSN), J1.28 (GPIO17), TP4.1
/cs_sd: J1.3 (GPIO1), JP11.2 (B), SD1.P2 (CD/DAT3), TP6.1
/cur_mess: IC4.14 (OUT4), J1.40 (GPIO28/ADC2), R10.1
/in+1: IC4.12 (IN4+), R7.1, R8.2
/in+2: IC4.1 (IN1+), R11.2, R12.1
/in-1: IC4.13 (IN4-), R9.1, R10.2
/in-2: IC4.15 (OUT1), IC4.16 (IN1-), J1.41 (GPIO29/ADC3)
/miso_lan: IC2.34 (MISO), J1.27 (GPIO16), TP5.1
/miso_sd: J1.2 (GPIO0), SD1.P7 (DAT0), TP8.1
/mosi_lan: IC2.35 (MOSI), J1.30 (GPIO19), TP3.1
/mosi_sd: J1.5 (GPIO3), SD1.P3 (CMD), TP9.1
/sck_lan: IC2.33 (SCLK), J1.29 (GPIO18), TP2.1
/sck_sd: J1.4 (GPIO2), SD1.P5 (CLK), TP7.1
/scl0: J1.37 (GPIO25), MUXH1.22 (SCL), scl1.4
/scl1: J1.39 (GPIO27/ADC1), scl0.4
/sda0: J1.36 (GPIO24), MUXH1.23 (SDA), scl1.5
/sda1: J1.38 (GPIO26/ADC0), scl0.5
/~USB_BOOT: J4.1, R66.2
GND: 3VLIN1.2 (GND_1), 3VLIN1.4 (GND_2), 3VLIN2.2 (GND_1), 3VLIN2.4 (GND_2), !V_BAT1.2, BUCK1.4 (GND), C1.2, C2.1, C3.1, C4.1, C5.1, C6.1, C7.1, C8.1, C9.1, C10.1, C11.1, C13.1, C14.1, C15.1, C16.1, C18.2, C19.2, C20.1, C21.1, C22.1, C23.1, C25.1, C26.2, C27.1, C28.1, C29.1, C30.1, C31.1, C32.1, C33.1, C34.1, C35.1, C36.2, C37.2, C38.2, C39.2, C40.2, C41.1, C42.1, C43.1, C44.2, C46.2, C47.2, C48.2, C49.2, C50.2, C51.2, C53.2, C54.2, C55.2, C56.2, C57.2, C58.2, C59.2, C60.2, C61.2, D5.2 (A), D9.2 (A), H1-2.1, H1-2.3, H1-2.5, H1-2.6, H3-8.2, H3-8.4, H3-8.6, H3-8.8, H3-8.10, H3-8.12, H3-8.MP1, H3-8.MP2, IC1.2 (~RE), IC1.5 (GND), IC2.3 (AGND_1), IC2.9 (AGND_2), IC2.14 (AGND_3), IC2.16 (AGND_4), IC2.19 (AGND_5), IC2.29 (GND), IC2.48 (AGND_6), IC4.11 (VCC-), IC4.17 (GND), IC5.4 (GND), ICH0.2 (GND), ICH1.2 (GND), ICH2.2 (GND), ICH3.2 (GND), ICH4.2 (GND), ICH5.2 (GND), ICH6.2 (GND), ICH7.2 (GND), J1.19 (TESTEN), J1.57 (GND), J2.5, J2.MP1, J2.MP2, J2.MP3, J2.MP4, J2.MP5, J2.MP6, J4.2, J5.9, J6.9, JH2.3 (B), JH3.3 (B), JH4.3 (B), JHVA1.1, JP1.1 (A), JP4.1 (A), MUXH1.2 (A1), MUXH1.3 (A2), MUXH1.12 (VSS), Ox0.1, Ox1.1, Ox2.1, Ox3.1, Ox4.1, Ox5.1, R6.1, R8.1, R12.2, R28.2, R30.1, S1.1 (NO_1), S1.4 (NO_2), S1.G1 (GND), SD1.G1 (GND_1), SD1.G2 (GND_2), SD1.G3 (GND_3), SD1.G4 (GND_4), SD1.G5 (GND_5), SD1.G6 (GND_6), SD1.G7 (GND_7), SD1.G8 (GND_8), SD1.G9 (GND_9), SD1.G10 (GND_10), SD1.P6 (VSS), U1.1 (GND), U2.4 (GND), V_5V1.1, V_BAT1.1, V_BATT1.1, V_LAN1.1, V_SD1.1, V_shifter1.11 (GND), V_uC1.1, Y1.2 (GND_1), Y1.4 (GND_2), Y2.2 (GND_1), Y2.4 (GND_2), scl0.3, scl1.3
unnamed: 3VLIN1.3 (OUT), C8.2, JP9.1 (A)
unnamed: 3VLIN2.3 (OUT), JP3.1 (A)
unnamed: !V_BAT1.1, R21.1
unnamed: BUCK1.6 (BST), C17.1
unnamed: BUCK1.8 (FB), R5.1, R6.2
unnamed: BUCK1.1 (RT), R28.1
unnamed: BUCK1.7 (SS), C3.2
unnamed: BUCK1.5 (SW), C17.2, L1.1
unnamed: C9.2, J3.2, R13.1
unnamed: C45.2, R38.2, R39.1
unnamed: C52.2, R37.2, R40.1
unnamed: C53.1, J3.5, R37.1, R38.1
unnamed: D5.1 (K), D7.2 (A)
unnamed: D8.2 (A), D9.1 (K)
unnamed: FB1.1, R13.2, R16.2, R31.2
unnamed: C29.2, IC2.22 (1V2O)
unnamed: IC2.26 (DUPLED), TP15.1
unnamed: IC2.10 (EXRES1), R30.2
unnamed: IC2.36 (INTN), TP16.1
unnamed: IC2.45 (PMODE0), JH4.2 (C)
unnamed: IC2.44 (PMODE1), JH3.2 (C)
unnamed: IC2.43 (PMODE2), JH2.2 (C)
unnamed: IC2.5 (RXN), R40.2
unnamed: IC2.6 (RXP), R39.2
unnamed: C31.2, IC2.20 (TOCAP)
unnamed: IC2.1 (TXN), R32.2
unnamed: IC2.2 (TXP), R33.2
unnamed: C25.2, IC5.3 (OUTPUT), JP5.1 (A)
unnamed: J1.17 (GPIO14), TP13.1
unnamed: J1.18 (GPIO15), TP14.1
unnamed: J1.31 (GPIO20), TP18.1
unnamed: J1.46 (USB_DM), R2.2
unnamed: J1.47 (USB_DP), R1.2
unnamed: J1.48 (USB_VDD), Jvbus1.2 (C)
unnamed: C10.2, J3.8 (GND), J3.13, J3.14
unnamed: J3.9, R15.2
unnamed: J3.11, R14.2
unnamed: J5.1, MUXH1.20 (IO1_7)
unnamed: J5.2, MUXH1.19 (IO1_6)
unnamed: J5.3, MUXH1.18 (IO1_5)
unnamed: J5.4, MUXH1.17 (IO1_4)
unnamed: J5.5, MUXH1.16 (IO1_3)
unnamed: J5.6, MUXH1.15 (IO1_2)
unnamed: J5.7, MUXH1.14 (IO1_1)
unnamed: J5.8, MUXH1.13 (IO1_0)
unnamed: F1.2, J5V2.2
unnamed: J6.1, MUXH1.4 (IO0_0)
unnamed: J6.2, MUXH1.5 (IO0_1)
unnamed: J6.3, MUXH1.6 (IO0_2)
unnamed: J6.4, MUXH1.7 (IO0_3)
unnamed: J6.5, MUXH1.8 (IO0_4)
unnamed: J6.6, MUXH1.9 (IO0_5)
unnamed: J6.7, MUXH1.10 (IO0_6)
unnamed: J6.8, MUXH1.11 (IO0_7)
unnamed: JH1.3 (B), JHVA1.2
unnamed: JP1.2 (C), JP11.1 (A), SD1.CD1
unnamed: JP4.2 (C), MUXH1.21 (A0)
unnamed: C39.1, JP10.1 (A), U1.2 (VO)
unnamed: LED1.3 (K_B), R36.1
unnamed: LED1.4 (K_G), R35.2
unnamed: LED1.2 (K_R), R34.2
unnamed: LED_OX1.3 (K_B), R26.1
unnamed: LED_OX1.4 (K_G), R25.2
unnamed: LED_OX1.2 (K_R), R4.2
unnamed: R17.1, V_LAN1.2
unnamed: R19.1, V_5V1.2
unnamed: R20.1, V_SD1.2
unnamed: R22.1, V_BATT1.2
unnamed: R24.1, V_uC1.2
unnamed: C24.1, V_shifter1.2 (VCCA)
unnamed: C12.2, V_shifter1.19 (VCCB)
unnamed: C16.2, R29.1, Y1.1 (IN/OUT)
unnamed: C37.1, R68.2, Y2.3 (XTAL_2)
VBUS: J2.1, JB_or_U1.1
V_Batt: D7.1 (K), D8.1 (K), R7.2, R11.1, R_shunt1.1, V_BAT1.2

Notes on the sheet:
Adapter to Ballon? https://www.digikey.de/de/products/detail/amphenol-industrial-operations/PT02E-8-4P/378756 hard to get :( -Reverse Voltage Protec?
Ferite
R11/R12 = 5/1
Adress(changeable) currently 0100000xB
Differenzverstärker: Vo = I * Rs * R10/R9 if R7 = R9 and R8 = R10 Imax = ca. 3.3A, Rs = 1mOhm; V0max = 3V3; R10/R9 = V0/(Imax*Rs) = 1k ->I = Vo/(Rs*2,5k)
bei 2mA 1.75V
ETHERNET
PROZESSING
Make sure C8 is close to pin 45 of RP2040
Oxygen Sensors
Make sure R3 and R4 are close to RP2040
StatusLED
HEATING
USB
POWER
LAN
Input
Reverse Voltage Protection
Current and Voltage tracking
Flash
only 100mA in a KS! And no damage to Ic!. But check for current spikes thouh frequenzy limited to ~1k though
Make sure C10 is close to pin 44 of RP2040
Buck
Reset
Messure
VCC wrong!!! Output Resistors Missing
Crystal

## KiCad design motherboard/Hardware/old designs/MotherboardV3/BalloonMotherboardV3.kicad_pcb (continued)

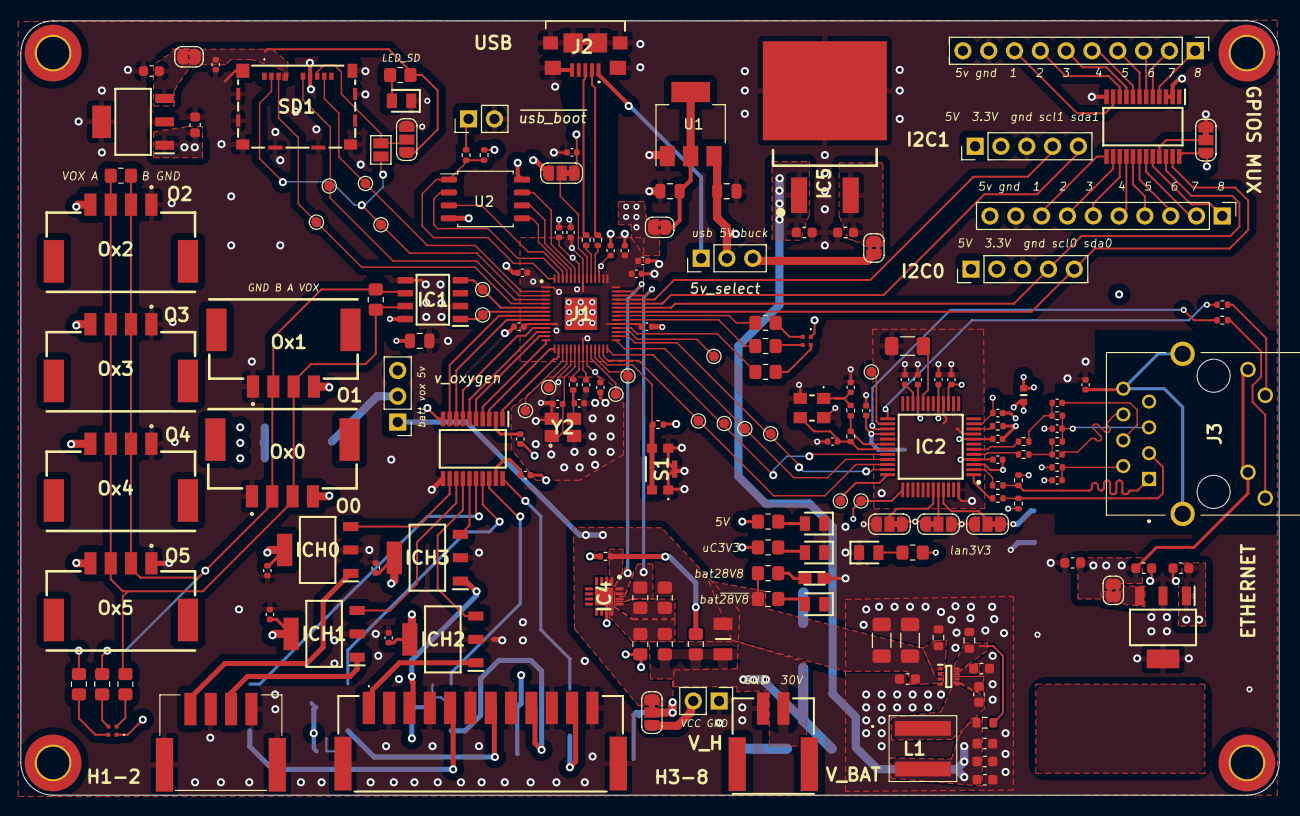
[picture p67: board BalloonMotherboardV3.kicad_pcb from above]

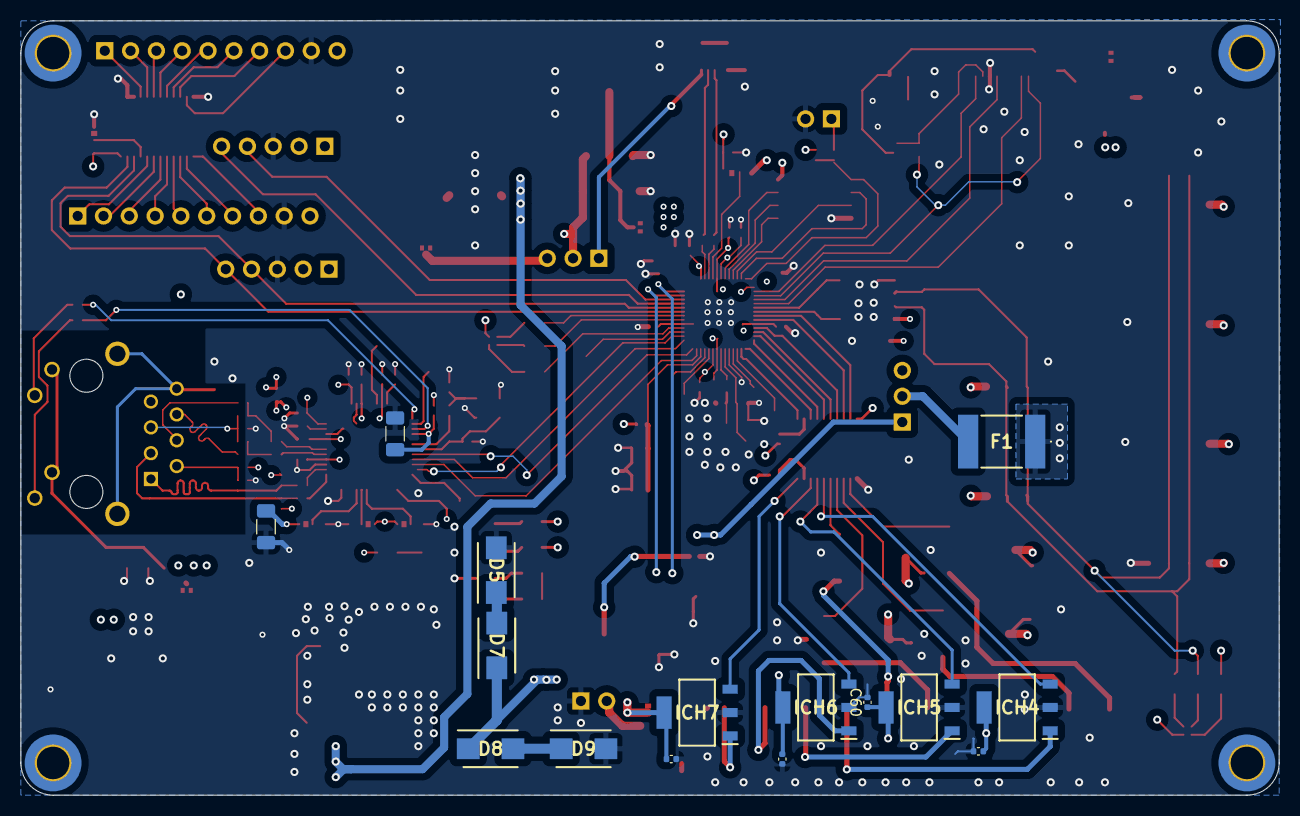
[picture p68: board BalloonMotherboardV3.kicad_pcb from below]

Board: 4 copper layers, 123.8 x 76.2 mm, 197 parts (15 on the bottom side), 156 nets.

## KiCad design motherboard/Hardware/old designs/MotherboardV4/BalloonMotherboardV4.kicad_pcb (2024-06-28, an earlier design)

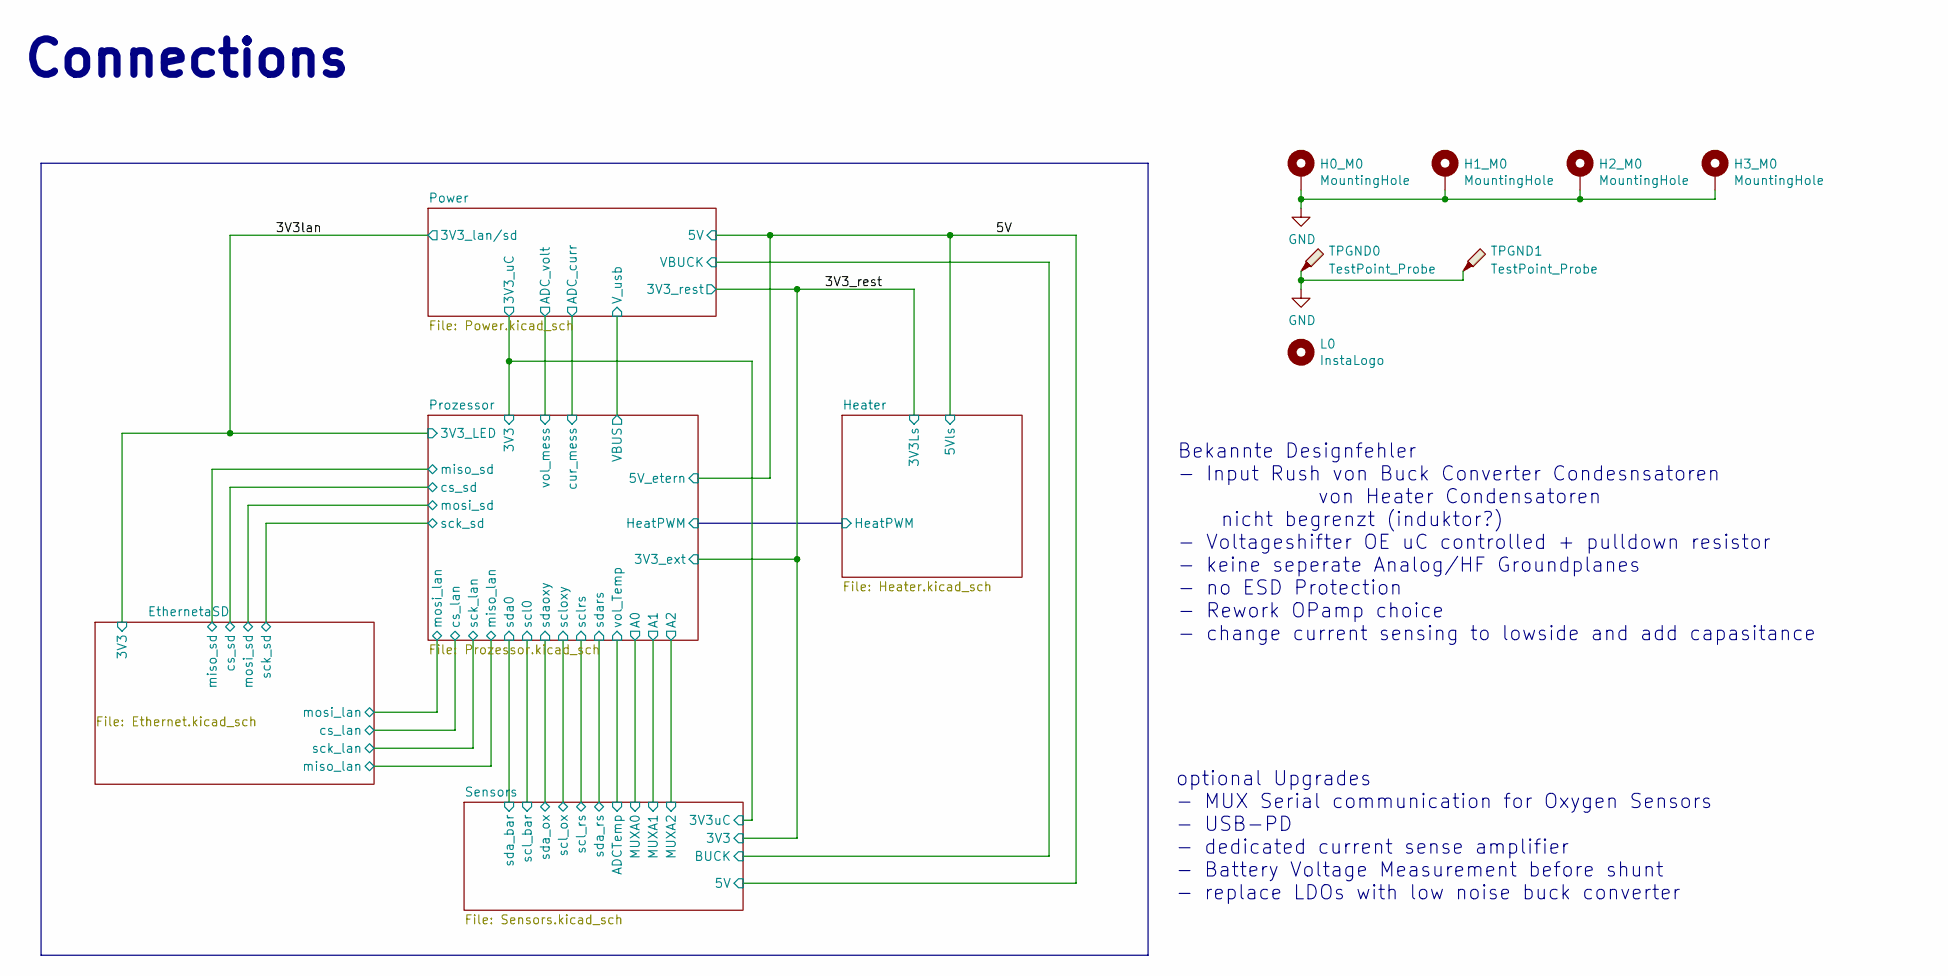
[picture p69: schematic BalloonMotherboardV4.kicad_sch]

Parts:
H0_M0, H1_M0, H2_M0, H3_M0: MountingHole; MountingHole_2.2mm_M2_Pad_Via
L0: InstaLogo; insta
TPGND0, TPGND1: TestPoint_Probe; TestPoint_Loop_D1.80mm_Drill1.0mm_Beaded

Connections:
GND: H0_M0.1, H1_M0.1, H2_M0.1, H3_M0.1, TPGND0.1, TPGND1.1; also elsewhere on the board

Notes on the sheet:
optional Upgrades - MUX Serial communication for Oxygen Sensors - USB-PD - dedicated current sense amplifier - Battery Voltage Measurement before shunt - replace LDOs with low noise buck converter
Bekannte Designfehler - Input Rush von Buck Converter Condesnsatoren von Heater Condensatoren nicht begrenzt (induktor?) - Voltageshifter OE uC controlled + pulldown resistor - keine seperate Analog/HF Groundplanes - no ESD Protection - Rework OPamp choice - change current sensing to lowside and ad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
Connections

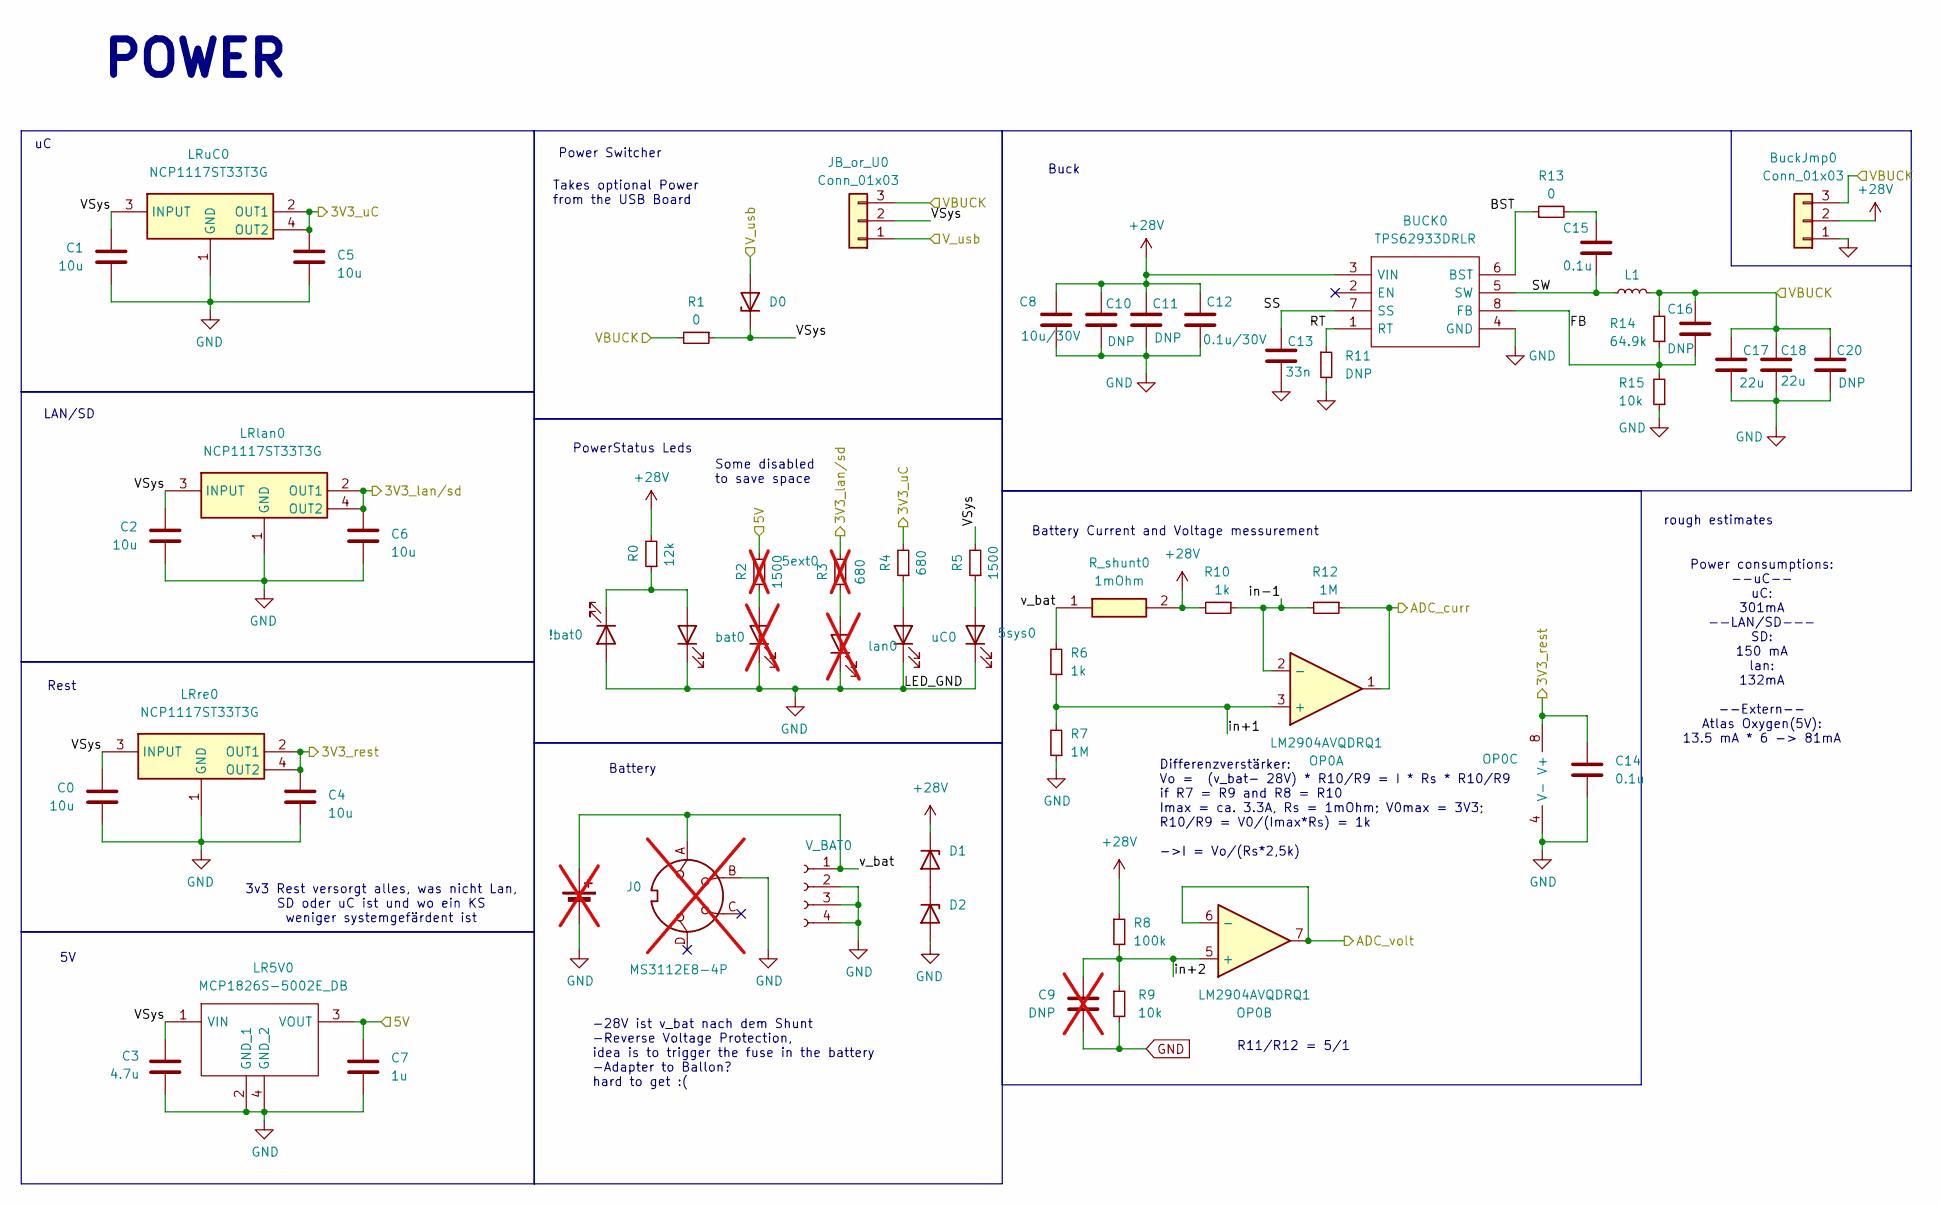
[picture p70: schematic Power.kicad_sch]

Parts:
5ext0: APTD2012LCGCK; LEDC2012X120N; Mouser Part Number 604-APTD2012LCGCK; not fitted
5sys0: APTD2012LCGCK; LEDC2012X120N; Mouser Part Number 604-APTD2012LCGCK
!bat0: APTD2012LSURCK; LEDM2012X120N; Mouser Part Number 604-APTD2012LSURCK
BT0: Battery_Cell; not fitted
BUCK0: TPS62933DRLR; SOTFL50P160X60-8N; Mouser Part Number 595-TPS62933DRLR
BuckJmp0: Conn_01x03; PinHeader_1x03_P2.54mm_Vertical
C0, C1, C2, C4, C5, C6: 10u; C_0805_2012Metric_Pad1.18x1.45mm_HandSolder
C3: 4.7u; C_0805_2012Metric_Pad1.18x1.45mm_HandSolder
C7: 1u; C_0402_1005Metric_Pad0.74x0.62mm_HandSolder
C8: 10u/30V; C_0805_2012Metric_Pad1.18x1.45mm_HandSolder
C9: DNP; C_0805_2012Metric_Pad1.18x1.45mm_HandSolder; not fitted
C10, C11, C20: DNP; C_0805_2012Metric_Pad1.18x1.45mm_HandSolder
C12: 0.1u/30V; C_0402_1005Metric_Pad0.74x0.62mm_HandSolder
C13: 33n; C_0805_2012Metric_Pad1.18x1.45mm_HandSolder
C14, C15: 0.1u; C_0402_1005Metric_Pad0.74x0.62mm_HandSolder
C16: DNP; C_0402_1005Metric_Pad0.74x0.62mm_HandSolder
C17, C18: 22u; C_0805_2012Metric_Pad1.18x1.45mm_HandSolder
D0, D1, D2: RBR2LB60BTBR1; DIOM5336X245N; Mouser Part Number 755-RBR2LB60BTBR1
J0: MS3112E8-4P; Mouser Part Number 654-MS3112E8-4P; not fitted
JB_or_U0: Conn_01x03; PinHeader_1x03_P2.54mm_Vertical
L1: 74439346068; Mouser Part Number 710-74439346068
LR5V0: MCP1826S-5002E_DB; SOT230P700X180-4N; Mouser Part Number 579-MCP1826S-5002EDB
LRlan0: NCP1117ST33T3G; SOT230P700X180-4N; Mouser Part Number 863-NCP1117ST33T3G
LRre0: NCP1117ST33T3G; SOT230P700X180-4N; Mouser Part Number 863-NCP1117ST33T3G
LRuC0: NCP1117ST33T3G; SOT230P700X180-4N; Mouser Part Number 863-NCP1117ST33T3G
OP0: LM2904AVQDRQ1; SOIC127P600X175-8N
R0: 12k; R_0603_1608Metric_Pad0.98x0.95mm_HandSolder
R1, R13: 0; R_0603_1608Metric_Pad0.98x0.95mm_HandSolder
R2: 1500; R_0603_1608Metric_Pad0.98x0.95mm_HandSolder; not fitted
R3: 680; R_0603_1608Metric_Pad0.98x0.95mm_HandSolder; not fitted
R4: 680; R_0603_1608Metric_Pad0.98x0.95mm_HandSolder
R5: 1500; R_0603_1608Metric_Pad0.98x0.95mm_HandSolder
R6, R10: 1k; R_0603_1608Metric_Pad0.98x0.95mm_HandSolder
R7, R12: 1M; R_0603_1608Metric_Pad0.98x0.95mm_HandSolder
R8: 100k; R_0603_1608Metric_Pad0.98x0.95mm_HandSolder
R9, R15: 10k; R_0603_1608Metric_Pad0.98x0.95mm_HandSolder
R11: DNP; R_0603_1608Metric_Pad0.98x0.95mm_HandSolder
R14: 64.9k; R_0603_1608Metric_Pad0.98x0.95mm_HandSolder
R_shunt0: 1mOhm; RESC3216X90N; Mouser Part Number 603-PA1206FRE7W0R01Z
V_BAT0: 502352-0200; 5023520200; Mouser Part Number 538-502352-0200
bat0: APTD2012LCGCK; LEDC2012X120N; Mouser Part Number 604-APTD2012LCGCK
lan0: APTD2012LCGCK; LEDC2012X120N; Mouser Part Number 604-APTD2012LCGCK; not fitted
uC0: APTD2012LCGCK; LEDC2012X120N; Mouser Part Number 604-APTD2012LCGCK

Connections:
+28V: BUCK0.3 (VIN), BuckJmp0.2, C8.2, C10.2, C11.2, C12.2, D1.1 (K), R0.2, R8.1, R10.2, R_shunt0.2; also elsewhere on the board
/3V3_rest: C4.2, C14.2, LRre0.2 (OUT1), LRre0.4 (OUT2), OP0.8 (V+); also elsewhere on the board
/3V3lan: C6.2, LRlan0.2 (OUT1), LRlan0.4 (OUT2), R3.2; also elsewhere on the board
/5V: C7.2, LR5V0.3 (VOUT), R2.2; also elsewhere on the board
/Power/3V3_uC: C5.2, LRuC0.2 (OUT1), LRuC0.4 (OUT2), R4.2; also elsewhere on the board
/Power/ADC_curr: OP0.1, R12.1; also elsewhere on the board
/Power/ADC_volt: OP0.6 (-), OP0.7; also elsewhere on the board
/Power/BST: BUCK0.6 (BST), R13.1
/Power/FB: BUCK0.8 (FB), C16.2, R14.1, R15.2
/Power/RT: BUCK0.1 (RT), R11.1
/Power/SS: BUCK0.7 (SS), C13.2
/Power/SW: BUCK0.5 (SW), C15.1, L1.1
/Power/VBUCK: BuckJmp0.3, C16.1, C17.2, C18.2, C20.2, JB_or_U0.3, L1.2, R1.2, R14.2; also elsewhere on the board
/Power/VSys: C0.2, C1.2, C2.2, C3.1, D0.1 (K), JB_or_U0.2, LR5V0.1 (VIN), LRlan0.3 (INPUT), LRre0.3 (INPUT), LRuC0.3 (INPUT), R1.1, R5.2
/Power/V_usb: D0.2 (A), JB_or_U0.1; also elsewhere on the board
/Power/in+1: OP0.3 (+), R6.1, R7.2
/Power/in+2: C9.2, OP0.5 (+), R8.2, R9.1
/Power/in-1: OP0.2 (-), R10.1, R12.2
/Power/v_bat: BT0.1 (+), J0.A, R6.2, R_shunt0.1, V_BAT0.1
GND: 5ext0.1 (K), 5sys0.1 (K), !bat0.2 (A), BT0.2 (-), BUCK0.4 (GND), BuckJmp0.1, C0.1, C1.1, C2.1, C3.2, C4.1, C5.1, C6.1, C7.1, C8.1, C9.1, C10.1, C11.1, C12.1, C13.1, C14.1, C17.1, C18.1, C20.1, D2.2 (A), J0.B, LR5V0.2 (GND_1), LR5V0.4 (GND_2), LRlan0.1 (GND), LRre0.1 (GND), LRuC0.1 (GND), OP0.4 (V-), R7.1, R9.2, R11.2, R15.1, V_BAT0.2, V_BAT0.3, V_BAT0.4, bat0.1 (K), lan0.1 (K), uC0.1 (K); also elsewhere on the board
unnamed: 5ext0.2 (A), R2.1
unnamed: 5sys0.2 (A), R5.1
unnamed: !bat0.1 (K), R0.1, bat0.2 (A)
unnamed: C15.2, R13.2
unnamed: D1.2 (A), D2.1 (K)
unnamed: R3.1, lan0.2 (A)
unnamed: R4.1, uC0.2 (A)

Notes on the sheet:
Power consumptions: --uC-- uC: 301mA --LAN/SD--- SD: 150 mA lan: 132mA --Extern-- Atlas Oxygen(5V): 13.5 mA * 6 -> 81mA
Rest
Differenzverstärker: Vo = (v_bat- 28V) * R10/R9 = I * Rs * R10/R9 if R7 = R9 and R8 = R10 Imax = ca. 3.3A, Rs = 1mOhm; V0max = 3V3; R10/R9 = V0/(Imax*Rs) = 1k ->I = Vo/(Rs*2,5k)
PowerStatus Leds
Power Switcher
LAN/SD
POWER
Battery
-28V ist v_bat nach dem Shunt -Reverse Voltage Protection, idea is to trigger the fuse in the battery -Adapter to Ballon? hard to get :(
rough estimates
Takes optional Power from the USB Board
Buck
Battery Current and Voltage messurement
3v3 Rest versorgt alles, was nicht Lan, SD oder uC ist und wo ein KS weniger systemgefärdent ist
R11/R12 = 5/1
Some disabled to save space

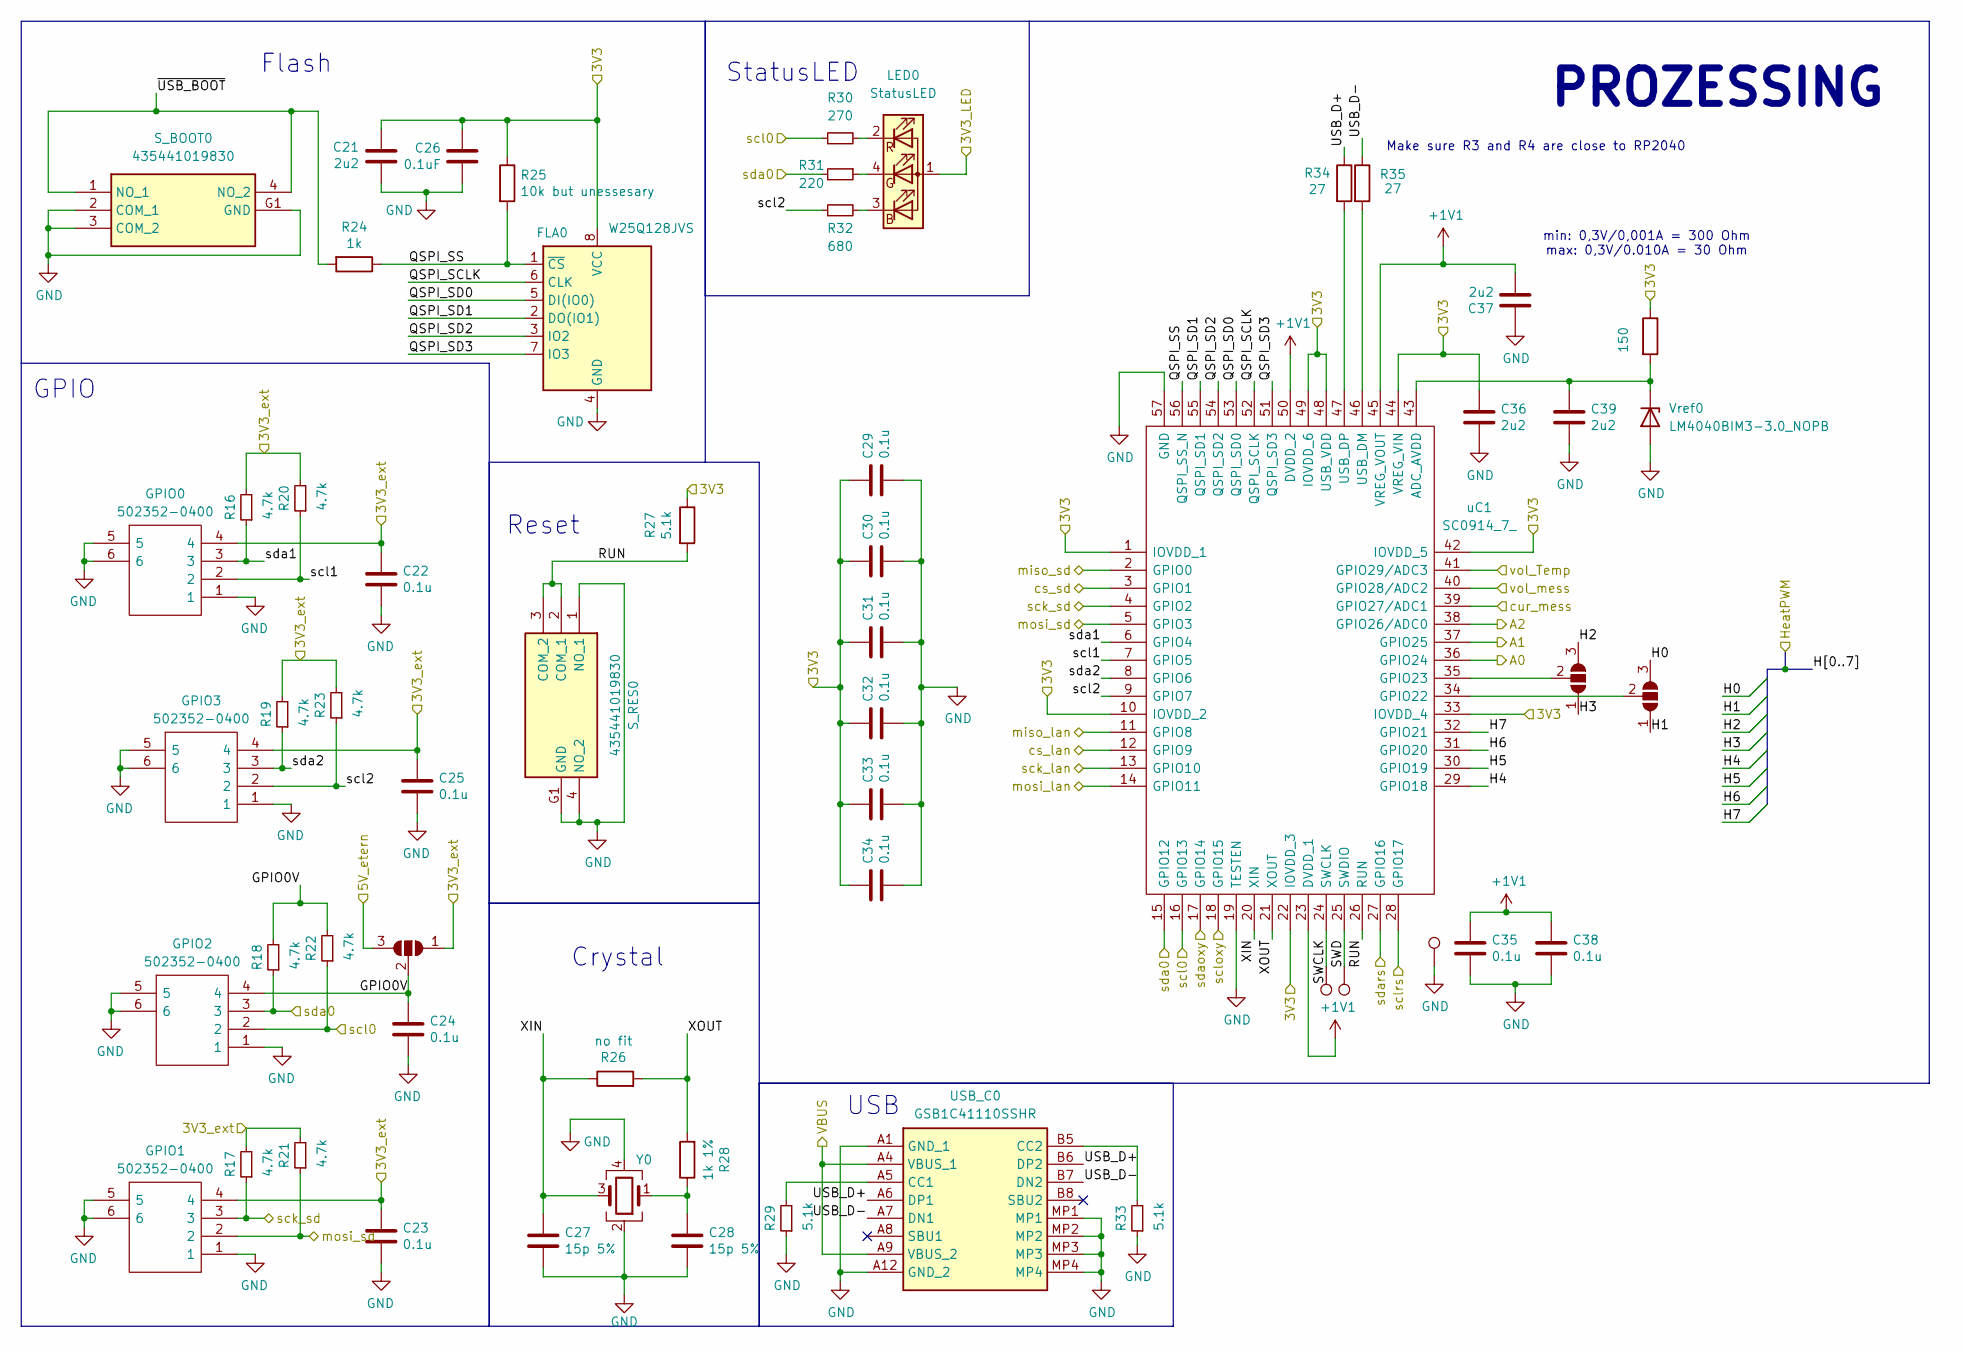
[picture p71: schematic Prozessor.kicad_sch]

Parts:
C21, C36, C37, C39: 2u2; C_0805_2012Metric_Pad1.18x1.45mm_HandSolder
C22, C23, C24, C25, C29, C30, C31, C32, C33, C34, C35, C38: 0.1u; C_0402_1005Metric_Pad0.74x0.62mm_HandSolder
C26: 0.1uF; C_0402_1005Metric_Pad0.74x0.62mm_HandSolder
C27, C28: 15p 5%; C_0402_1005Metric_Pad0.74x0.62mm_HandSolder
FLA0: W25Q128JVS; SOIC-8_5.23x5.23mm_P1.27mm
GPIO0, GPIO1, GPIO2, GPIO3: 502352-0400; 5023520400; Mouser Part Number 538-502352-0400
JP0, JP1, JP2: SolderJumper_3_Open; SolderJumper-3_P1.3mm_Open_RoundedPad1.0x1.5mm_NumberLabels
LED0: StatusLED; LTRBR37G4R4S01250; Mouser Part Number 720-LTRBR37GA6714
R16, R17, R18, R19, R20, R21, R22, R23: 4.7k; R_0603_1608Metric_Pad0.98x0.95mm_HandSolder
R24: 1k; R_0603_1608Metric_Pad0.98x0.95mm_HandSolder
R25: 10k but unessesary; R_0603_1608Metric_Pad0.98x0.95mm_HandSolder
R26: no fit; R_0402_1005Metric_Pad0.72x0.64mm_HandSolder
R27, R29, R33: 5.1k; R_0603_1608Metric_Pad0.98x0.95mm_HandSolder
R28: 1k 1%; R_0603_1608Metric_Pad0.98x0.95mm_HandSolder
R30: 270; R_0603_1608Metric_Pad0.98x0.95mm_HandSolder
R31: 220; R_0603_1608Metric_Pad0.98x0.95mm_HandSolder
R32: 680; R_0603_1608Metric_Pad0.98x0.95mm_HandSolder
R34, R35: 27; R_0603_1608Metric_Pad0.98x0.95mm_HandSolder
R36: 150; R_0603_1608Metric_Pad0.98x0.95mm_HandSolder
S_BOOT0: 435441019830; Mouser Part Number 710-435441019830
S_RES0: 435441019830; Mouser Part Number 710-435441019830
TP0, TP1, TP2: TestPoint; TestPoint_Pad_D1.0mm
USB_C0: GSB1C41110SSHR; Manufacturer_Part_Number GSB1C41110SSHR
Vref0: LM4040BIM3-3.0_NOPB; SOT95P237X112-3N; Mouser Part Number 926-LM4040BIM330NOPB
Y0: ABM8G-12.000MHZ-4Y-T3; ABM8G; Mouser Part Number 815-ABM8G-12-4YT3
uC1: SC0914_7_; QFN40P700X700X90-57N-D; Mouser Part Number 358-SC09147

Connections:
+1V1: C35.1, C37.2, C38.1, uC1.23 (DVDD_1), uC1.45 (VREG_VOUT), uC1.50 (DVDD_2)
/3V3_rest: C22.1, C23.1, C25.1, GPIO0.4, GPIO1.4, GPIO3.4, JP0.1 (A), R16.2, R17.2, R19.2, R20.2, R21.2, R23.2; also elsewhere on the board
/3V3lan: LED0.1 (A); also elsewhere on the board
/5V: JP0.3 (B); also elsewhere on the board
/EthernetaSD/cs_lan: uC1.12 (GPIO9); also elsewhere on the board
/EthernetaSD/cs_sd: uC1.3 (GPIO1); also elsewhere on the board
/EthernetaSD/miso_lan: uC1.11 (GPIO8); also elsewhere on the board
/EthernetaSD/miso_sd: uC1.2 (GPIO0); also elsewhere on the board
/EthernetaSD/mosi_lan: uC1.14 (GPIO11); also elsewhere on the board
/EthernetaSD/mosi_sd: GPIO1.2, R21.1, uC1.5 (GPIO3); also elsewhere on the board
/EthernetaSD/sck_lan: uC1.13 (GPIO10); also elsewhere on the board
/EthernetaSD/sck_sd: GPIO1.3, R17.1, uC1.4 (GPIO2); also elsewhere on the board
/Heater/H0: JP2.3 (B); also elsewhere on the board
/Heater/H1: JP2.1 (A); also elsewhere on the board
/Heater/H2: JP1.3 (B); also elsewhere on the board
/Heater/H3: JP1.1 (A); also elsewhere on the board
/Heater/H4: uC1.29 (GPIO18); also elsewhere on the board
/Heater/H5: uC1.30 (GPIO19); also elsewhere on the board
/Heater/H6: uC1.31 (GPIO20); also elsewhere on the board
/Heater/H7: uC1.32 (GPIO21); also elsewhere on the board
/Power/3V3_uC: C21.2, C26.1, C29.1, C30.1, C31.1, C32.1, C33.1, C34.1, C36.1, FLA0.8 (VCC), R25.1, R27.1, R36.1, uC1.1 (IOVDD_1), uC1.10 (IOVDD_2), uC1.22 (IOVDD_3), uC1.33 (IOVDD_4), uC1.42 (IOVDD_5), uC1.44 (VREG_VIN), uC1.48 (USB_VDD), uC1.49 (IOVDD_6); also elsewhere on the board
/Power/ADC_curr: uC1.39 (GPIO27/ADC1); also elsewhere on the board
/Power/ADC_volt: uC1.40 (GPIO28/ADC2); also elsewhere on the board
/Power/V_usb: USB_C0.A4 (VBUS_1), USB_C0.A9 (VBUS_2); also elsewhere on the board
/Prozessor/A0: uC1.36 (GPIO24); also elsewhere on the board
/Prozessor/A1: uC1.37 (GPIO25); also elsewhere on the board
/Prozessor/A2: uC1.38 (GPIO26/ADC0); also elsewhere on the board
/Prozessor/GPIO0V: C24.1, GPIO2.4, JP0.2 (C), R18.2, R22.2
/Prozessor/QSPI_SCLK: FLA0.6 (CLK), uC1.52 (QSPI_SCLK)
/Prozessor/QSPI_SD0: FLA0.5 (DI(IO0)), uC1.53 (QSPI_SD0)
/Prozessor/QSPI_SD1: FLA0.2 (DO(IO1)), uC1.55 (QSPI_SD1)
/Prozessor/QSPI_SD2: FLA0.3 (IO2), uC1.54 (QSPI_SD2)
/Prozessor/QSPI_SD3: FLA0.7 (IO3), uC1.51 (QSPI_SD3)
/Prozessor/QSPI_SS: FLA0.1 (~CS), R24.1, R25.2, uC1.56 (QSPI_SS_N)
/Prozessor/RUN: R27.2, S_RES0.2 (COM_1), S_RES0.3 (COM_2), uC1.26 (RUN)
/Prozessor/SWCLK: TP0.1, uC1.24 (SWCLK)
/Prozessor/SWD: TP1.1, uC1.25 (SWDIO)
/Prozessor/USB_D+: R34.1, USB_C0.A6 (DP1), USB_C0.B6 (DP2)
/Prozessor/USB_D-: R35.1, USB_C0.A7 (DN1), USB_C0.B7 (DN2)
/Prozessor/XIN: C27.1, R26.1, Y0.3, uC1.20 (XIN)
/Prozessor/XOUT: R26.2, R28.2, uC1.21 (XOUT)
/Prozessor/scl0: GPIO2.2, R22.1, R30.1, uC1.16 (GPIO13); also elsewhere on the board
/Prozessor/scl1: GPIO0.2, R20.1, uC1.7 (GPIO5)
/Prozessor/scl2: GPIO3.2, R23.1, R32.1, uC1.9 (GPIO7)
/Prozessor/scloxy: uC1.18 (GPIO15); also elsewhere on the board
/Prozessor/sclrs: uC1.28 (GPIO17); also elsewhere on the board
/Prozessor/sda0: GPIO2.3, R18.1, R31.2, uC1.15 (GPIO12); also elsewhere on the board
/Prozessor/sda1: GPIO0.3, R16.1, uC1.6 (GPIO4)
/Prozessor/sda2: GPIO3.3, R19.1, uC1.8 (GPIO6)
/Prozessor/sdaoxy: uC1.17 (GPIO14); also elsewhere on the board
/Prozessor/sdars: uC1.27 (GPIO16); also elsewhere on the board
/Prozessor/vol_Temp: uC1.41 (GPIO29/ADC3); also elsewhere on the board
/Prozessor/~USB_BOOT: R24.2, S_BOOT0.1 (NO_1), S_BOOT0.4 (NO_2)
GND: C21.1, C22.2, C23.2, C24.2, C25.2, C26.2, C27.2, C28.2, C29.2, C30.2, C31.2, C32.2, C33.2, C34.2, C35.2, C36.2, C37.1, C38.2, C39.2, FLA0.4 (GND), GPIO0.1, GPIO0.5, GPIO0.6, GPIO1.1, GPIO1.5, GPIO1.6, GPIO2.1, GPIO2.5, GPIO2.6, GPIO3.1, GPIO3.5, GPIO3.6, R29.1, R33.1, S_BOOT0.2 (COM_1), S_BOOT0.3 (COM_2), S_BOOT0.G1 (GND), S_RES0.1 (NO_1), S_RES0.4 (NO_2), S_RES0.G1 (GND), TP2.1, USB_C0.A1 (GND_1), USB_C0.A12 (GND_2), USB_C0.MP1, USB_C0.MP2, USB_C0.MP3, USB_C0.MP4, Vref0.2 (A), Y0.2, Y0.4, uC1.19 (TESTEN), uC1.57 (GND); also elsewhere on the board
unnamed: C28.1, R28.1, Y0.1
unnamed: JP1.2 (C), uC1.35 (GPIO23)
unnamed: JP2.2 (C), uC1.34 (GPIO22)
unnamed: LED0.3 (BK), R32.2
unnamed: LED0.4 (GK), R31.1
unnamed: LED0.2 (RK), R30.2
unnamed: R29.2, USB_C0.A5 (CC1)
unnamed: R33.2, USB_C0.B5 (CC2)
unnamed: C39.1, R36.2, Vref0.1 (K), uC1.43 (ADC_AVDD)
unnamed: R35.2, uC1.46 (USB_DM)
unnamed: R34.2, uC1.47 (USB_DP)

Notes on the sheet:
Reset
min: 0,3V/0,001A = 300 Ohm max: 0,3V/0.010A = 30 Ohm
StatusLED
Crystal
Flash
USB
Make sure R3 and R4 are close to RP2040
PROZESSING
GPIO

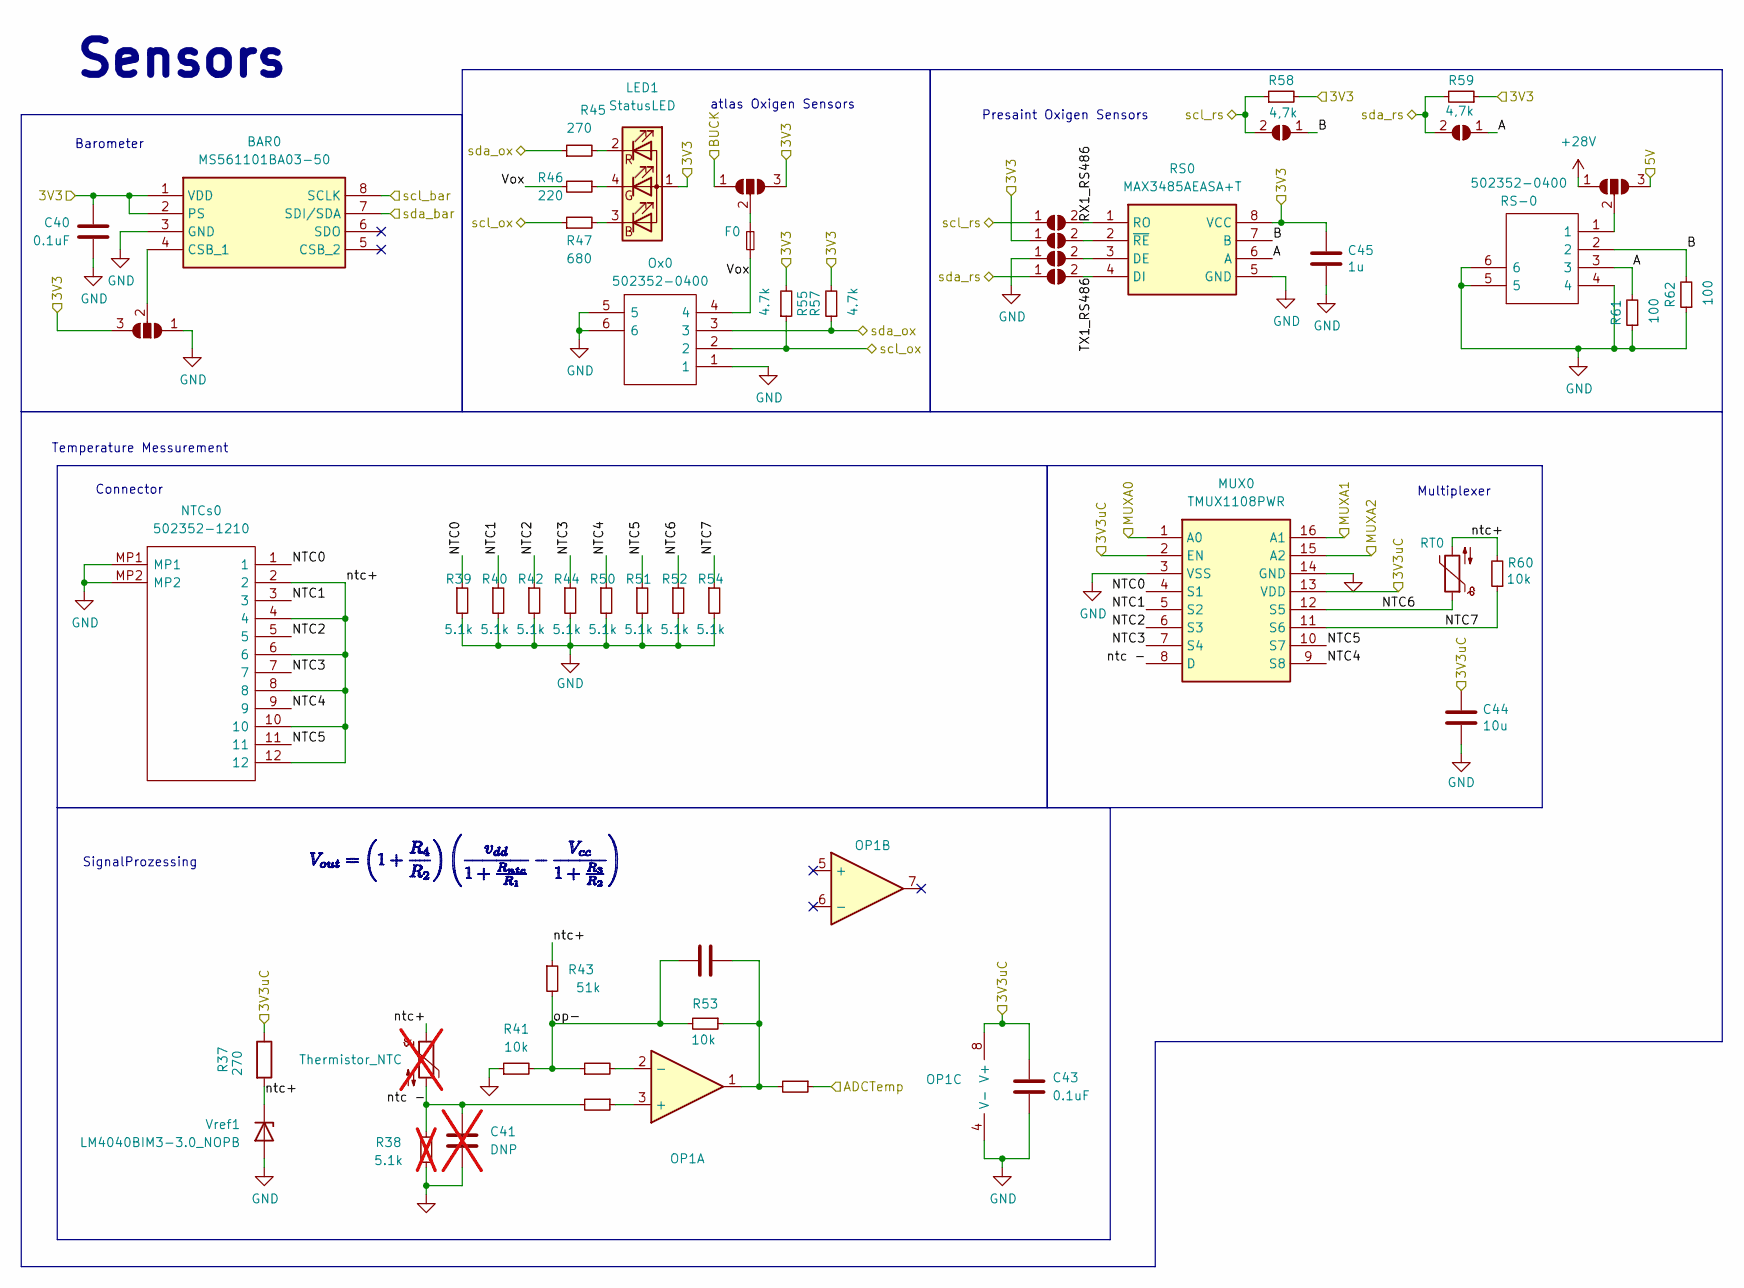
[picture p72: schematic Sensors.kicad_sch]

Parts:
BAR0: MS561101BA03-50; Mouser Part Number 824-MS561101BA03-50
C40, C43: 0.1uF; C_0402_1005Metric_Pad0.74x0.62mm_HandSolder
C41: DNP; C_0402_1005Metric_Pad0.74x0.62mm_HandSolder; not fitted
C42: DNP; C_0402_1005Metric_Pad0.74x0.62mm_HandSolder
C44: 10u; C_0805_2012Metric_Pad1.18x1.45mm_HandSolder
C45: 1u; C_0402_1005Metric_Pad0.74x0.62mm_HandSolder
F0: MF-FSML100_8-2; FUSC1608X70N; Mouser Part Number 652-MF-FSML100/8-2
JP3, JP4, JP5, JP6, JP7, JP8: SolderJumper_2_Open; SolderJumper-2_P1.3mm_Open_RoundedPad1.0x1.5mm
JP9: SolderJumper_3_Open; SolderJumper-3_P1.3mm_Open_RoundedPad1.0x1.5mm_NumberLabels
JPVOX0, JPVOX1: SolderJumper_3_Open; SolderJumper-3_P1.3mm_Open_RoundedPad1.0x1.5mm_NumberLabels
LED1: StatusLED; LTRBR37G4R4S01250; Mouser Part Number 720-LTRBR37GA6714
MUX0: TMUX1108PWR; SOP65P640X120-16N; Mouser Part Number 595-TMUX1108PWR
NTCs0: 502352-1210; 5023521210; Mouser Part Number 538-502352-1210
OP1: TLV9002QDRQ1; SOIC127P600X175-8N
Ox0: 502352-0400; 5023520400; Mouser Part Number 538-502352-0400
R37, R45: 270; R_0603_1608Metric_Pad0.98x0.95mm_HandSolder
R38: 5.1k; R_0603_1608Metric_Pad0.98x0.95mm_HandSolder; not fitted
R39, R40, R42, R44, R50, R51, R52, R54: 5.1k; R_0603_1608Metric_Pad0.98x0.95mm_HandSolder
R41, R53, R60: 10k; R_0603_1608Metric_Pad0.98x0.95mm_HandSolder
R43: 51k; R_0603_1608Metric_Pad0.98x0.95mm_HandSolder
R46: 220; R_0603_1608Metric_Pad0.98x0.95mm_HandSolder
R47: 680; R_0603_1608Metric_Pad0.98x0.95mm_HandSolder
R48, R49, R56: 1k; R_0603_1608Metric_Pad0.98x0.95mm_HandSolder
R55, R57: 4.7k; R_0603_1608Metric_Pad0.98x0.95mm_HandSolder
R58, R59: 4,7k; R_0603_1608Metric_Pad0.98x0.95mm_HandSolder
R61, R62: 100; R_0603_1608Metric_Pad0.98x0.95mm_HandSolder
RS0: MAX3485AEASA+T; SOIC127P600X175-8N; Mouser Part Number 700-MAX3485AEASA+T
RS-0: 502352-0400; 5023520400; Mouser Part Number 538-502352-0400
RT0: NTCGS163JF103FT8; THRMC1608X90N; Mouser Part Number 810-NTCGS163JF103FT8
TH0: Thermistor_NTC; not fitted
Vref1: LM4040BIM3-3.0_NOPB; SOT95P237X112-3N; Mouser Part Number 926-LM4040BIM330NOPB

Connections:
+28V: JP9.1 (A); also elsewhere on the board
/3V3_rest: BAR0.1 (VDD), BAR0.2 (PS), C40.2, C45.1, JP4.1 (A), JPVOX0.3 (B), JPVOX1.3 (B), LED1.1 (A), R55.2, R57.2, R58.2, R59.1, RS0.8 (VCC); also elsewhere on the board
/5V: JP9.3 (B); also elsewhere on the board
/Power/3V3_uC: C43.2, C44.1, MUX0.2 (EN), MUX0.13 (VDD), OP1.8 (V+), R37.1; also elsewhere on the board
/Power/VBUCK: JPVOX1.1 (A); also elsewhere on the board
/Prozessor/A0: MUX0.1 (A0); also elsewhere on the board
/Prozessor/A1: MUX0.16 (A1); also elsewhere on the board
/Prozessor/A2: MUX0.15 (A2); also elsewhere on the board
/Prozessor/scl0: BAR0.8 (SCLK); also elsewhere on the board
/Prozessor/scloxy: Ox0.2, R47.1, R55.1; also elsewhere on the board
/Prozessor/sclrs: JP3.1 (A), JP7.2 (B), R58.1; also elsewhere on the board
/Prozessor/sda0: BAR0.7 (SDI/SDA); also elsewhere on the board
/Prozessor/sdaoxy: Ox0.3, R45.1, R57.1; also elsewhere on the board
/Prozessor/sdars: JP6.1 (A), JP8.2 (B), R59.2; also elsewhere on the board
/Prozessor/vol_Temp: R56.1; also elsewhere on the board
/Sensors/A: JP8.1 (A), R61.2, RS0.6 (A), RS-0.3
/Sensors/B: JP7.1 (A), R62.2, RS0.7 (B), RS-0.2
/Sensors/NTC0: MUX0.4 (S1), NTCs0.1, R39.1
/Sensors/NTC1: MUX0.5 (S2), NTCs0.3, R40.1
/Sensors/NTC2: MUX0.6 (S3), NTCs0.5, R42.1
/Sensors/NTC3: MUX0.7 (S4), NTCs0.7, R44.1
/Sensors/NTC4: MUX0.9 (S8), NTCs0.9, R50.1
/Sensors/NTC5: MUX0.10 (S7), NTCs0.11, R51.1
/Sensors/NTC6: MUX0.12 (S5), R52.1, RT0.1
/Sensors/NTC7: MUX0.11 (S6), R54.1, R60.1
/Sensors/RX1_RS486: JP3.2 (B), RS0.1 (RO)
/Sensors/TX1_RS486: JP6.2 (B), RS0.4 (DI)
/Sensors/Vox: F0.1, Ox0.4, R46.2
/Sensors/ntc -: C41.2, MUX0.8 (D), R38.1, R49.2, TH0.2
/Sensors/ntc+: NTCs0.2, NTCs0.4, NTCs0.6, NTCs0.8, NTCs0.10, NTCs0.12, R37.2, R43.1, R60.2, RT0.2, TH0.1, Vref1.1 (K)
/Sensors/op-: C42.2, R41.2, R43.2, R48.1, R53.2
GND: BAR0.3 (GND), C40.1, C41.1, C43.1, C44.2, C45.2, JP5.1 (A), JPVOX0.1 (A), MUX0.3 (VSS), MUX0.14 (GND), NTCs0.MP1, NTCs0.MP2, OP1.4 (V-), Ox0.1, Ox0.5, Ox0.6, R38.2, R39.2, R40.2, R41.1, R42.2, R44.2, R50.2, R51.2, R52.2, R54.2, R61.1, R62.1, RS0.5 (GND), RS-0.4, RS-0.5, RS-0.6, Vref1.2 (A); also elsewhere on the board
unnamed: BAR0.4 (CSB_1), JPVOX0.2 (C)
unnamed: C42.1, OP1.1, R53.1, R56.2
unnamed: JP4.2 (B), RS0.2 (~RE)
unnamed: JP5.2 (B), RS0.3 (DE)
unnamed: JP9.2 (C), RS-0.1
unnamed: F0.2, JPVOX1.2 (C)
unnamed: LED1.3 (BK), R47.2
unnamed: LED1.4 (GK), R46.1
unnamed: LED1.2 (RK), R45.2
unnamed: OP1.3 (+), R49.1
unnamed: OP1.2 (-), R48.2

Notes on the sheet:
atlas Oxigen Sensors
Connector
Multiplexer
Temperature Messurement
Sensors
Barometer
SignalProzessing
Presaint Oxigen Sensors

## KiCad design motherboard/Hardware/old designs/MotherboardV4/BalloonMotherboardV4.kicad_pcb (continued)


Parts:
C46, C50, C51, C52, C53, C54, C55, C63: 0.1u; C_0402_1005Metric_Pad0.74x0.62mm_HandSolder
C47, C56: 10uF/16V; C_0805_2012Metric_Pad1.18x1.45mm_HandSolder
C48, C57: 10n; C_0805_2012Metric_Pad1.18x1.45mm_HandSolder
C49: 4.7u; C_0805_2012Metric_Pad1.18x1.45mm_HandSolder
C58, C59: 6.8n; C_0805_2012Metric_Pad1.18x1.45mm_HandSolder
C60: 22nF; C_0805_2012Metric_Pad1.18x1.45mm_HandSolder
C61, C65: 18p; C_0402_1005Metric_Pad0.74x0.62mm_HandSolder
C62: 2u2; C_0805_2012Metric_Pad1.18x1.45mm_HandSolder
C64: 1nF/200V; C_0805_2012Metric_Pad1.18x1.45mm_HandSolder
FB0: BLM18SP102SZ1D; BLM18SP221SN1B; Mouser Part Number 81-BLM18SP102SZ1D
J1: J1B1211CCD; Mouser Part Number 950-J1B1211CCD
JH0, JH1, JH2: Jumper_3_Bridged12; SolderJumper-3_P1.3mm_Bridged12_RoundedPad1.0x1.5mm_NumberL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
LAN1: W5500; QFP50P900X900X160-48N; Mouser Part Number 950-W5500
R63: 12.4k 1%; R_0603_1608Metric_Pad0.98x0.95mm_HandSolder
R64, R65, R66, R68, R73: 0R; R_0603_1608Metric_Pad0.98x0.95mm_HandSolder
R67, R69, R70, R71: 49R9 1%; R_0603_1608Metric_Pad0.98x0.95mm_HandSolder
R72: 10R 1%; R_0603_1608Metric_Pad0.98x0.95mm_HandSolder
R74: 1M; R_0603_1608Metric_Pad0.98x0.95mm_HandSolder
R75, R76, R77, R78: 10k; R_0603_1608Metric_Pad0.98x0.95mm_HandSolder
R79, R80: 330; R_0603_1608Metric_Pad0.98x0.95mm_HandSolder
SD0: 693072010801; Mouser Part Number 710-693072010801
TP3, TP4: TestPoint; TestPoint_Pad_D1.0mm
Y1: ECS-250-6-33B2-CTP-TR; ECS250633B2CTPTR; Mouser Part Number 520-250-6-33B2-CTPTR

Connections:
/3V3lan: C46.2, C47.2, C50.2, C51.2, C52.2, C53.2, C54.2, C55.2, C56.2, C62.2, C63.1, FB0.2, J1.10, J1.12, JH0.1 (A), JH1.1 (A), JH2.1 (A), LAN1.4 (AVDD_1), LAN1.8 (AVDD_2), LAN1.11 (AVDD_3), LAN1.15 (AVDD_4), LAN1.17 (AVDD_5), LAN1.21 (AVDD_6), LAN1.28 (VDD), LAN1.37 (RSTN), R75.2, R76.2, R77.2, R78.2, SD0.4 (VDD); also elsewhere on the board
/EthernetaSD/E0: JH2.2 (C), LAN1.45 (PMODE0)
/EthernetaSD/E1: JH1.2 (C), LAN1.44 (PMODE1)
/EthernetaSD/E2: JH0.2 (C), LAN1.43 (PMODE2)
/EthernetaSD/F-: FB0.1, R70.2, R71.2, R72.2
/EthernetaSD/LED_LAN_A: LAN1.27 (ACTLED), R80.1
/EthernetaSD/LED_LAN_B: LAN1.25 (LINKLED), R79.1
/EthernetaSD/RCT: C57.1, J1.5 (RCT), R67.1, R69.1
/EthernetaSD/RXN: C58.1, J1.6 (RD-)
/EthernetaSD/RXP: C59.1, J1.4 (RD+)
/EthernetaSD/TCT: C60.2, J1.2 (TCT), R72.1
/EthernetaSD/TXN: J1.3 (TD-), R68.1, R70.1
/EthernetaSD/TXP: J1.1 (TD+), R65.1, R71.1
/EthernetaSD/XI: LAN1.30 (XI/CLKIN), R73.2, R74.1
/EthernetaSD/Xo: C65.2, LAN1.31 (XO), R74.2, Y1.3 (OUT/IN)
/EthernetaSD/cs_lan: LAN1.32 (SCSN); also elsewhere on the board
/EthernetaSD/cs_sd: R78.1, SD0.2 (DAT3/CD); also elsewhere on the board
/EthernetaSD/miso_lan: LAN1.34 (MISO); also elsewhere on the board
/EthernetaSD/miso_sd: R75.1, SD0.7 (DAT0); also elsewhere on the board
/EthernetaSD/mosi_lan: LAN1.35 (MOSI); also elsewhere on the board
/EthernetaSD/mosi_sd: R77.1, SD0.3 (CMD); also elsewhere on the board
/EthernetaSD/sck_lan: LAN1.33 (SCLK); also elsewhere on the board
/EthernetaSD/sck_sd: R76.1, SD0.5 (CLK); also elsewhere on the board
GND: C46.1, C47.1, C48.1, C49.1, C50.1, C51.1, C52.1, C53.1, C54.1, C55.1, C56.1, C57.2, C60.1, C61.1, C62.1, C63.2, C64.1, C65.1, JH0.3 (B), JH1.3 (B), JH2.3 (B), LAN1.3 (AGND_1), LAN1.9 (AGND_2), LAN1.14 (AGND_3), LAN1.16 (AGND_4), LAN1.19 (AGND_5), LAN1.29 (GND), LAN1.48 (AGND_6), R63.1, SD0.6 (VSS), SD0.MP1, SD0.MP2, SD0.MP3, SD0.MP4, Y1.2 (GND_1), Y1.4 (GND_2); also elsewhere on the board
unnamed: C58.2, R64.1, R69.2
unnamed: C59.2, R66.1, R67.2
unnamed: C64.2, J1.8, J1.13, J1.14
unnamed: J1.9, R80.2
unnamed: J1.11, R79.2
unnamed: C48.2, LAN1.22 (1V2O)
unnamed: LAN1.26 (DUPLED), TP4.1
unnamed: LAN1.10 (EXRES1), R63.2
unnamed: LAN1.36 (INTN), TP3.1
unnamed: LAN1.5 (RXN), R64.2
unnamed: LAN1.6 (RXP), R66.2
unnamed: C49.2, LAN1.20 (TOCAP)
unnamed: LAN1.1 (TXN), R68.2
unnamed: LAN1.2 (TXP), R65.2
unnamed: C61.2, R73.1, Y1.1 (IN/OUT)

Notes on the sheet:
ETHERNET


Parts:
C66, C70: 0.1u; C_0402_1005Metric
C67, C68, C69, C71, C73, C74, C76, C77: 0.22u (grob); C_0402_1005Metric
C72: 1u/30V DNP; C_0805_2012Metric_Pad1.18x1.45mm_HandSolder
C75: 0.1u/30V DNP; C_0805_2012Metric_Pad1.18x1.45mm_HandSolder
F1, F2, F3, F4, F5, F6, F7, F8: MF-FSML100_8-2; FUSC1608X70N; Mouser Part Number 652-MF-FSML100/8-2
H0, H1, H2, H3, H4, H5, H6, H7: ITS4200S-ME-O; SOT230P700X170-4N; Mouser Part Number 726-ITS4200S-ME-O
H1-0: 502352-0400; 5023520400; Mouser Part Number 538-502352-0400
H3-0: 502352-1210; 5023521210; Mouser Part Number 538-502352-1210
JHEAT0: PinHeader_2.54mm; PinHeader_1x02_P2.54mm_Vertical
R81, R82, R83, R87, R88, R89, R93, R94: Heater; not fitted
R84, R85, R86, R90, R91, R92, R95, R96: 100; R_0603_1608Metric_Pad0.98x0.95mm_HandSolder
Vshi0: TXS0108EQPWRQ1; SOP65P640X120-20N; Mouser Part Number 595-TXS0108EQPWRQ1

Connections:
+28V: JHEAT0.2; also elsewhere on the board
/3V3_rest: C66.1, Vshi0.2 (VCCA), Vshi0.10 (OE); also elsewhere on the board
/5V: C70.1, Vshi0.19 (VCCB); also elsewhere on the board
/Heater/H0: Vshi0.9 (A8); also elsewhere on the board
/Heater/H1: Vshi0.8 (A7); also elsewhere on the board
/Heater/H2: Vshi0.7 (A6); also elsewhere on the board
/Heater/H3: Vshi0.6 (A5); also elsewhere on the board
/Heater/H4: Vshi0.5 (A4); also elsewhere on the board
/Heater/H5: Vshi0.4 (A3); also elsewhere on the board
/Heater/H6: Vshi0.3 (A2); also elsewhere on the board
/Heater/H7: Vshi0.1 (A1); also elsewhere on the board
/Heater/H:0: R84.2, Vshi0.13 (B7)
/Heater/H:1: R85.2, Vshi0.12 (B8)
/Heater/H:2: R86.2, Vshi0.20 (B1)
/Heater/H:3: R90.2, Vshi0.18 (B2)
/Heater/H:4: R91.2, Vshi0.17 (B3)
/Heater/H:5: R92.2, Vshi0.16 (B4)
/Heater/H:6: R95.2, Vshi0.15 (B5)
/Heater/H:7: R96.2, Vshi0.14 (B6)
/Heater/H_0: F1.2, H1-0.4, R81.1
/Heater/H_1: F2.2, H1-0.2, R82.1
/Heater/H_2: F3.2, H3-0.1, R83.1
/Heater/H_3: F4.2, H3-0.3, R87.1
/Heater/H_4: F5.2, H3-0.5, R88.1
/Heater/H_5: F6.2, H3-0.7, R89.1
/Heater/H_6: F7.2, H3-0.9, R93.1
/Heater/H_7: F8.2, H3-0.11, R94.1
/Heater/Vs_Heat: C67.1, C68.1, C69.1, C71.1, C72.2, C73.1, C74.1, C75.1, C76.1, C77.1, H0.4 (VS), H1.4 (VS), H2.4 (VS), H3.4 (VS), H4.4 (VS), H5.4 (VS), H6.4 (VS), H7.4 (VS), JHEAT0.1
GND: C66.2, C67.2, C68.2, C69.2, C70.2, C71.2, C72.1, C73.2, C74.2, C75.2, C76.2, C77.2, H0.2 (GND), H1.2 (GND), H1-0.1, H1-0.3, H1-0.5, H1-0.6, H2.2 (GND), H3.2 (GND), H3-0.2, H3-0.4, H3-0.6, H3-0.8, H3-0.10, H3-0.12, H3-0.MP1, H3-0.MP2, H4.2 (GND), H5.2 (GND), H6.2 (GND), H7.2 (GND), R81.2, R82.2, R83.2, R87.2, R88.2, R89.2, R93.2, R94.2, Vshi0.11 (GND); also elsewhere on the board
unnamed: H0.3 (IN), R84.1
unnamed: F1.1, H0.1 (OUT)
unnamed: H1.3 (IN), R85.1
unnamed: F2.1, H1.1 (OUT)
unnamed: H2.3 (IN), R86.1
unnamed: F3.1, H2.1 (OUT)
unnamed: H3.3 (IN), R90.1
unnamed: F4.1, H3.1 (OUT)
unnamed: H4.3 (IN), R91.1
unnamed: F5.1, H4.1 (OUT)
unnamed: H5.3 (IN), R92.1
unnamed: F6.1, H5.1 (OUT)
unnamed: H6.3 (IN), R95.1
unnamed: F7.1, H6.1 (OUT)
unnamed: H7.3 (IN), R96.1
unnamed: F8.1, H7.1 (OUT)

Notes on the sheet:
Voltage Shifter
Profet Switcher
Source Selector
Mosfet calculation, !obsolite in this design! GPIOs can source up to 12mA, but per default 4. So assuming 4mA and 3.3V, the Gate Resistors of the MOSEDS have to be minimum 8250Ohm -> lets use 1k
These are Profet smart switcher wich power the heating elements according to the PWM signal they recieve
HEATING
Connector



Board: 4 copper layers, 85.9 x 82.0 mm, 256 parts (94 on the bottom side), 171 nets.

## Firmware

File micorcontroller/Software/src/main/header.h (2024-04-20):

#ifndef HEADER_H
#define HEADER_H

#include <Arduino.h>

#define DEBUG 1
#define USB_ENABLE 1
#define MICROS 1

#if DEBUG == 1
#define debug(x) Serial.print(x)
#define debugln(x) Serial.println(x)

#if MICROS == 1
#define MESSURETIME_START        \
    unsigned long ta = micros(); \
    unsigned long tb;
#define MESSURETIME_STOP \
    debug("-Time:");     \
    tb = micros() - ta;  \
    debug(tb);           \
    debug("us");
#else
#define MESSURETIME_START        \
    unsigned long ta = millis(); \
    unsigned long tb;
#define MESSURETIME_STOP \
    debug("-Time:");     \
    tb = millis() - ta;  \
    debug(tb);           \
    debug("ms");
#endif

#else
#define debug(x)
#define debugln(x)
#define MESSURETIME_START
#define MESSURETIME_STOP
#endif

/*----------------Pin mapping-------------*/
#define MISO_LAN 0 // 16
#define CS_LAN 1   // 17
#define SCK_LAN 2  // 18
#define MOSI_LAN 3 // 19

#define MISO_SD 0
#define MOSI_SD 3
#define CS_SD 1
#define SCK_SD 2

#define PIN_H0 6
#define PIN_H1 7
#define PIN_H2 8
#define PIN_H3 9
#define PIN_H4 10
#define PIN_H5 11
#define PIN_H6 12
#define PIN_H7 13

#define STATLED_R 23 // Status LeD pins
#define STATLED_G 22
#define STATLED_B 21

#define PIN_VOLT A3
#define PIN_CURR A2

/*struct_packet*/
extern volatile unsigned long id_struct;
struct packet
{ // struct_format L L 6L 6f 6f 6i i f 2i 80s
    unsigned long id = 0;
    unsigned long timestampPacket = 0;

    unsigned long timestampOxy[6] = {0};

    float oxigen[6] = {0.0f};
    float tempTube[6] = {0.0f};

    int heaterPWM[6] = {0};
    int error = 0;

    float tempCpu = analogReadTemp(3.3f);
    unsigned long power[2] = {0};

    char info[80] = {0};
};
struct packet packet_create();
char *packettochar(struct packet data);
void packet_print(struct packet pkt);
void packet_writeinfo(struct packet &data, const char *info);

/*i2c scan*/
void scan_wire();

/*tcp_client*/
extern char TCP_init;
void test_TCP_manually();
void setup_TCP_Client();
void send_TCP(char *data, unsigned long int size);
void recieve_TCP_command();
int send_TCP_packet(struct packet data);
uint8_t cabletest();
void testServer();

/*sd*/
extern char SD_init;
void init_SD();
int sd_numpackets(const char filepath[]);
bool writestruct(struct packet s_out, const char filepath[]);
bool readstruct(struct packet *data, const char filepath[], unsigned long position);
bool printfile(const char filepath[]);

/*thermal*/
#define HEAT_FREQ 1000          // 5kmax for the facy Ics
#define HEAT_HUNDERTPERCENT 100 // value where the heaters are fully turned on
#define HEAT_CURRENT 317        // aproximation of the current of a single Heater in mA

extern char heat_init;
void heat_initialize();
void heat_updateall(uint16_t *HeaterPWM);
void heat_updateone(uint8_t PIN, uint16_t PWM);
void heat_testmanual();
uint8_t heat_testauto();

/*status*/
uint32_t get_Status();

/*utilitly functions*/
unsigned long get_batvoltage();
unsigned long get_current();
void serial_commands();
void StatusLedBlink();
void blinkLed();
void fadeLED();
void heartbeat();

/*single File USB*/
extern char singleFileUsb_init;
void usb_singlefile_setup();
void usb_singlefile_update();
void headerCSV();
void plug(uint32_t i);
void unplug(uint32_t i);
void deleteCSV(uint32_t i);
void singlefile_close();
#endif

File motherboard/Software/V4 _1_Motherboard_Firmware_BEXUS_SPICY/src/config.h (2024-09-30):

/*--------config file----------------*/
#ifndef CONFIG_H
#define CONFIG_H

#include "Arduino.h"

/*Debug*/
#define DEBUG_MODE 2 /**activates debug statements. \
0 = disable                                         \
1 = Serial                                          \
2 = TCP -> dosn´t print error of tcp connection    \
3 = Serial & TCP*/

#define DEBUG_LEVEL 3 /*changes the debug console prints. \
0 = just errors                                           \
1 = Status Updates and sucess                             \
2 = Infos about running code                              \
3 = Debug infos                                           \
4 = state infos*/

#define DEBUG_COLOUR 1 /*activates/deactivates colour in debug outputs. \
Can decrease bandwith when colors disabled.*/

/*ADC/Analog Write*/
const float ADC_REF = 3.0;                               // reference voltage of the adc converter
const unsigned int ADC_RES = 12;                         // adc resolution in bit
const unsigned int ADC_MAX_READ = (pow(2, ADC_RES) - 1); // values adc generates when adc_ref voltage is applied to adc
const unsigned int ADC_MAX_WRITE = 100;                  // value where analogRrite = 100% duty cycle
const unsigned int ADC_FREQ_WRITE = 30000;               // frequency of adc write. therefore of the heater

/*Timeouts*/
const unsigned long TIMEOUT_WATCHDOG = 4000;     // in ms. 8000ms maximal
const unsigned long TIMEOUT_TCP_CONNECTION = 20; // conntection timeout of the tcp client
const unsigned long TIMEOUT_LIGHT_SENSOR = 100;  // timeout i2c connection light sensor
const unsigned long TIMEOUT_OXY_SERIAL = 500;    // timeout usart oxygen

/*Heating*/
const float HEAT_VOLTAGE = 7.7459666;                                   // in V
const float HEAT_RESISTANCE = 12;                                       // in Ohm
const float HEAT_CURRENT = HEAT_VOLTAGE / HEAT_RESISTANCE;              // current of a single Heater in A
const float HEAT_POWER = HEAT_CURRENT * HEAT_CURRENT * HEAT_RESISTANCE; // max heating power of a single heater                        // max PID value. is normed on heating_power

/*FD-OEM Oxygen sensor*/
const unsigned long COMMAND_LENGTH_MAX = 100; // how long a command string can possibly be
const unsigned long RETURN_LENGTH_MAX = 100;  // how long a return string can possibly be
const unsigned long OXY_BAUD = 19200;         // baud of oxygen usart connection

/*PI controller*/
const float SET_TEMP_DEFAULT = 20;                  // temperature target for PI controller. Set to -1000000.0 to disable Controller
const float KP_DEFAULT = 3.301;                   // set to -100000.0 to disable heaters on startup
const float KI_DEFAULT = 0.0322;                        // default values for integral gain
const float I_MAX_DEFAULT = 1.0;                      // default max value for integral
const float PI_MAX_DEFAULT = HEAT_POWER;              // defalut max heating power for pi controller
const unsigned long PI_T = 1000;                      // time in ms till next PID controller update. (1/Frequency of PI Controller)

const unsigned long PI_SWEEP_PRINT_DELAY = 60 * 1000; // delay between printout of PI_SWEEP

/*light sensors*/
#include "Adafruit_LTR390.h"
const ltr390_gain_t LIGHT_LTR390_GAIN = LTR390_GAIN_6;
const float LIGHT_LTR390_WFAC = 1;
const float LIGHT_LTR390_INT = 4;
const float LIGHT_LTR390_UV_SENSITIFITY = 2300;

/*Pin mapping*/
typedef enum
{
    // GPIO extension buses
    SDA0 = 2, // I2C Data Line 0
    SCL0 = 3, // I2C Clock Line 0

    SDA1 = 4, // I2C Data Line 1
    SCL1 = 5, // I2C Clock Line 1

    // LAN and SD card connected on SPI0 Bus
    CS_LAN = 17,    // Chip Select for LAN
    CS_SD = 16,     // Chip Select for SD Card
    MISO_SPI0 = 20, // Master In Slave Out for SPI0
    SCK_SPI0 = 18,  // Serial Clock for SPI0
    MOSI_SPI0 = 19, // Master Out Slave In for SPI0

    // V4.0 pins (commented out)
    // MISO_SPI0 = 0,
    // CS_SD = 1,
    // SCK_SPI0 = 2,
    // MOSI_SPI0 = 3,
    // LAN_MISO = 8,
    // CS_LAN = 9,
    // LAN_MOSI = 11,
    // LAN_SCK = 10,

    // High pins
    PIN_H0 = 8,
    PIN_H1 = 9,
    PIN_H2 = 10,
    PIN_H3 = 11,
    PIN_H4 = 12,
    PIN_H5 = 13,
    PIN_H6 = 14,
    PIN_H7 = 15,

    // Multiplexer lines for temperature probes and oxygen sensors
    PIN_MUX_ADRES_0 = 26,     // Multiplexer Select Line 0
    PIN_MUX_ADRES_1 = 25,     // Multiplexer Select Line 1
    PIN_MUX_ADRES_2 = 24,     // Multiplexer Select Line 2
    PIN_MUX_OXY_DISABLE = 21, // Multiplexer Oxygen Disable

    PIN_TEMPADC = A3, // Analog-to-Digital Converter for temperature

    NTC_OR_OxY_0 = 1, // S1 of MUX
    NTC_OR_OxY_1 = 2, // S2 of MUX
    NTC_OR_OxY_2 = 3, // S3 of MUX
    NTC_OR_OxY_3 = 4, // S4 of MUX
    NTC_4 = 8,        // S8 of MUX
    NTC_5 = 7,        // S7 of MUX
    NTC_SMD = 5,      // S5 of MUX
    NTC_10kfix = 6,   // S6 of MUX

    OxY_4 = 5,
    OxY_5 = 6,

    PIN_OX_RX = 0, // Oxygen Sensor RX
    PIN_OX_TX = 1, // Oxygen Sensor TX

    STATLED = 23, // Status LED

    PIN_VOLT = A2, // Voltage Pin
    PIN_CURR = A1, // Current Pin

    // Connection of the Light Sensor
    PIN_LIGHT_SDA_0 = SDA0, // I2C Data Line for Light Sensor AS7262
    PIN_LIGHT_SCL_0 = SCL0, // I2C Clock Line for Light Sensor AS7262

    PIN_LIGHT_SDA_1 = SDA1, // I2C Data Line for Light Sensor AS7263
    PIN_LIGHT_SCL_1 = SCL1  // I2C Clock Line for Light Sensor AS7263
} PIN_MAPPING;

/*errors*/
enum ERRORS
{
    ERROR_SD_INI,
    ERROR_SD_COUNT,
    ERROR_WR_STR,
    ERROR_SD_WRITE_OPEN,
    ERROR_SD_PINMAP,

    ERROR_TCP_INI,
    ERROR_TCP_COMMAND_PARSING,
    ERROR_TCP_PARAM_CORRUPT,
    ERROR_TCP_COMMAND_CORRUPT,
    ERROR_TCP_SEND_FAILED,
    ERROR_TCP_SEND_TIMEOUT,
    ERROR_TCP_SERVER_INVALID,
    ERROR_TCP_TRUNCATED,
    ERROR_TCP_TRUNCATED_2,
    ERROR_TCP_CABLE_DISCO,
    ERROR_TCP_NO_RESPONSE,
    ERROR_TCP_DEBUG_MEMORY,
    ERROR_TCP_CLIENT_CONNTECION,
    ERROR_TCP_SEND_MULTIBLE_FAILED,

    ERROR_HEAT_INI,

    ERROR_LIGHT_INI,

    ERROR_NO_NTC_CONNECTED,

    ERROR_STATE,

    ERROR_PACK_ID_OV,
    ERROR_PACK_MEM_AL,
    ERROR_PACKAGE_FREE_TWICE,

    ERROR_OXY_INI,
    ERROR_OXY_AUTO_AMP,
    ERROR_OXY_SIGNAL_INT_LOW,
    ERROR_OXY_OPTICAL_DETECTOR_SATURATED,
    ERROR_OXY_REF_SIGNAL_LOW,
    ERROR_OXY_REF_SIGNAL_HIGH,
    ERROR_OXY_SAMPLE_TEMP_SENSOR,
    ERROR_OXY_RESERVED,
    ERROR_OXY_HIGH_HUMIDITY,
    ERROR_OXY_CASE_TEMP_SENSOR,
    ERROR_OXY_PRESSURE_SENSOR,
    ERROR_OXY_HUMIDITY_SENSOR
};

/*parometer testing*/
#define BAROMETER_TEATING 0
#endif

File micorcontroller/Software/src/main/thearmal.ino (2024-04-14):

/*manages the heating elements*/
#define PIN_H0 6
#define PIN_H1 7
#define PIN_H2 8
#define PIN_H3 9
#define PIN_H4 10
#define PIN_H5 11
#define PIN_H6 12
#define PIN_H7 13

#define HEAT_FREQ 1000          // 5kmax for the facy Ics
#define HEAT_HUNDERTPERCENT 100 // value where the heaters are fully turned on
#define HEAT_CURRENT 317        // aproximation of the current of a single Heater in mA

char heat_init = 0;

/*initializes the pins, freq and range of the heating elements*/
void heat_initialize()
{
  analogWriteFreq(HEAT_FREQ); // 100Hz to 1MHz
  analogWriteRange(HEAT_HUNDERTPERCENT);
  pinMode(PIN_H0, OUTPUT);
  pinMode(PIN_H1, OUTPUT);
  pinMode(PIN_H2, OUTPUT);
  pinMode(PIN_H3, OUTPUT);
  pinMode(PIN_H4, OUTPUT);
  pinMode(PIN_H5, OUTPUT);
  heat_init = 1;
}

/**
 * /updates the PWM Dutycicle of the Heaters. Will not change PWM values wich are set to 1.
 * @param unsigned int HeaterPWM[] the PWM in an array
 */
void heat_updateall(uint16_t *HeaterPWM)
{
  if (!heat_init)
  {
    heat_initialize();
  }
  // analogWriteResolution
  heat_updateone(PIN_H0, HeaterPWM[0]);
  heat_updateone(PIN_H1, HeaterPWM[1]);
  heat_updateone(PIN_H2, HeaterPWM[2]);
  heat_updateone(PIN_H3, HeaterPWM[3]);
  heat_updateone(PIN_H4, HeaterPWM[4]);
  heat_updateone(PIN_H5, HeaterPWM[5]);
  heat_updateone(PIN_H6, HeaterPWM[6]);
  heat_updateone(PIN_H7, HeaterPWM[7]);
}

/**
 * Updates one Heater if the PWM value is not set to 1
 */
void heat_updateone(uint8_t PIN, uint16_t PWM)
{
  if (!heat_init)
  {
    heat_initialize();
  }

  if (PWM != 1)
  {
    analogWrite(PIN, PWM);
  }
}

/**
 * Sets all heaters on different PWM duticycles
 */
void heat_testmanual()
{
  debugln("<Manual Heater Test>");
  debugln("sets heater 1 to 10%, 2 to 20% and so on");
  debug("first Heater Pin: ");
  debugln(PIN_H0);
  if (!heat_init)
  {
    heat_initialize();
  }
  uint16_t buf[] = {10, 20, 30, 40, 50, 60,70,80};
  heat_updateall(buf);
}

/*can evalue the functionality fo individual heaters via the currentdraw
@return:*/
uint8_t heat_testauto()
{
  uint16_t buf[] = {0, 0, 0, 0, 0, 0};
  heat_updateall(buf);

  uint8_t results = 0;
  unsigned long cur_alloff = get_current(); // current with all heater off
  unsigned long cur_one;

  for (uint8_t i = 0; i < 6; i++)
  {
    buf[i] = HEAT_HUNDERTPERCENT;
    heat_updateall(buf);
    cur_one = get_current() - cur_alloff;
    if (HEAT_CURRENT - 30 < cur_one < HEAT_CURRENT + 30)
    {
      results |= (1 << i);
    }
    buf[i] = 0;
  }
  return results;
}

void updatePID()
{
  // float p,i,d;
}

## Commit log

2024-02-27 added uC Code and Groundstation python link
    [data.csv, rawdata.csv]
2024-02-28 Added Event listener for csv. Added Database Python Class for MongoDB. Added functions for database insertion
2024-03-01 database access
    [data.csv]
2024-03-02 updates Serverv3
    [data.csv]
2024-03-02 Added feature to MongoDB, more than one sensor collection now possible with the same class-method implemented it in Serverv3 but not active
    [data.csv]
2024-03-04 Added Model Funktion for Sensor and getAllData Function. Tested Database connection read and write
2024-03-13 adding automated heating tests
2024-03-17 added atlas sensor compability
2024-03-18 broke TCP server <skull emogi>
    [data.csv]
2024-03-25 some shifting around
    [Ballon_motherboard_V2.kicad_pcb, Ballon_motherboard_V2.kicad_sch, BalloonMotherboardV3-B_Adhesive.gbr, BalloonMotherboardV3-B_Courtyard.gbr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]
2024-03-25 better circuit pictures
2024-03-25 changed scematic picture
    [SD.kicad_sch]
2024-03-26 some moving around
    [Ballon_motherboard_V2.kicad_pcb, Ballon_motherboard_V2.kicad_sch, BalloonMotherboardV3-B_Adhesive.gbr, BalloonMotherboardV3-B_Courtyard.gbr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]
2024-04-03 added NTC calculation
    [BalloonMotherboardV4.kicad_pcb, BalloonMotherboardV4.kicad_sch, Ethernet.kicad_sch, Heater.kicad_sch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]
2024-04-03 some spicy planuml updates
    [BalloonMotherboardV4.kicad_pcb]
2024-04-11 propper Serial Comand System added
    [BalloonMotherboardV4.kicad_pcb, NTC Calculations.xlsx, Power.kicad_sch, Prozessor.kicad_sch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]
2024-04-14 added a serial command field for easy debugging
    [BalloonMotherboardV4-B_Cu.gbr, BalloonMotherboardV4-B_Mask.gbr, BalloonMotherboardV4-B_Paste.gbr, BalloonMotherboardV4-B_Silkscreen.gbr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]
2024-04-19 Switch to header BASED C file system {headache incomming}
    [BalloonMotherboardV4.kicad_pcb, BalloonMotherboardV4.kicad_sch, Ethernet.kicad_sch, Heater.kicad_sch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]
2024-04-20 rought prototype SingleFileUsb added
2024-04-26 startup message
    [BalloonMotherboardV4.xlsx, Power.kicad_sch, Sensors.kicad_sch]
2024-05-12 added uplink
    [216990-0003.stp, 2174507-2.stp, 435441019830.stp, 502352-0200.stp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]
2024-05-23 changed debug to level based debug and started writing driver for FD-OEM Module
    [216990-0003.stp, 2174507-2.stp, 435441019830.stp, 502352-0200.stp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]
2024-06-28 trying to fix things
    [BalloonMotherboardV4.kicad_pcb, BalloonMotherboardV4.kicad_sch, BalloonMotherboardV4.xlsx, Ethernet.kicad_sch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]
2024-06-28 clean some things up
    [Ballon_motherboard_V2.kicad_pcb, Ballon_motherboard_V2.kicad_sch, data.csv, untitled.kicad_sch]
2024-07-02 trying to fix2
    [Cable Harness.xlsx]
2024-07-02 renamend mirocontroller in motherboard
    [BalloonMotherboardV3-B_Adhesive.gbr, BalloonMotherboardV3-B_Courtyard.gbr, BalloonMotherboardV3-B_Cu.gbr, BalloonMotherboardV3-B_Fab.gbr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]
2024-07-03 changed opamp
    [BalloonMotherboardV4.1.kicad_sch, Sensors.kicad_sch]
2024-07-03 refined thermal controller
    [BalloonMotherboardV4.1.kicad_sch, Prozessor.kicad_sch, Sensors.kicad_sch]
2024-07-04 thermal calcuation
    [Boom MOtherboardV4.1 pretty.xlsx, Power.xlsx, benchmarks.csv]
2024-07-07 working on thermal
    [BalloonMotherboardV4.1.kicad_sch, ESA_2W5_V2.csv, Sensors.kicad_sch]
2024-07-07 worked on thermals
    [BalloonMotherboardV4.1.kicad_sch, ESA_2W5_V2.csv, ESA_2W5_cooled.csv, ESA_2W5_cooled.xlsx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]
2024-07-08 temperature update
    [ESA_2W5_cooled.csv]
2024-07-12 got oxygensensor switching and measuring reliably
    [data.csv]
2024-07-24 added inrush current limiter
    [FD-OEM Case.3mf, Inrush_current_limiter-F_Cu.dxf, Inrush_current_limiter.dsn, Inrush_current_limiter.kicad_pcb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]
2024-07-25 Frontend Plot for Ox Sensor working, needs to update on new Data though
2024-07-25 Added all oxgen Sensors, UI and a little bit of spicy-style *
2024-07-26 fixing pin issue with USART
2024-07-26 updated light sensors
    [BalloonMotherboardV4.1.kicad_sch]
2024-07-28 tweaked sd managment
    [data.csv, data[148].bin.csv]
2024-07-29 worked on thepi controller
    [ESA_2W5_V2.csv, ESA_2W5_cooled.csv, ESA_2W5_cooled.xlsx, data[148].bin.csv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]
2024-08-06 added optional pressure sensor
    [BalloonMotherboardV4.1.kicad_sch, Heater.kicad_sch, Sensors.kicad_sch]
2024-08-12 refinig server
    [rawdata.bin.csv, temp_log[71][8].csv, temp_step_respons[57][2.50000].csv, temp_step_respons[71][2.50].csv]
2024-08-17 changed pi controller form static values to struct based to enable more than one sensor at once
2024-08-18 changed folder
    [Power.xlsx]
2024-08-19 reworked printf statements
2024-08-20 random python stuff
    [temp_log[71][8].csv, temp_step_respons[57][2.50000].csv, temp_step_respons[71][2.50].csv]
2024-08-21 added ota update
    [Power.xlsx]
2024-08-26 added light sensors
2024-09-01 updates pre TVAC
    [live_plot.xlsx]
2024-09-24 changed to add light sensors
2024-09-25 changed print error line
2024-09-30 ip change
    [TVAC_sucessfull.xlsx]
2024-10-19 removed bloat
    [BalloonMotherboardV3-B_Adhesive.gbr, BalloonMotherboardV3-B_Courtyard.gbr, BalloonMotherboardV3-B_Cu.gbr, BalloonMotherboardV3-B_Fab.gbr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]
